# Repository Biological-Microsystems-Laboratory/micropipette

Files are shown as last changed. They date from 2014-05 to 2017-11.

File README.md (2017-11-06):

3D Printable Micropipette
=========================

This printable micropipette actuates a disposable syringe to an adjustable set-point using an assembly of 3D-printable parts and basic hardware.





## Parts

Both the 30-300 uL Pipette and the 100-1000 uL Pipette use the same printed parts: body-clip.stl and plunger.stl. In addition a disposable syringe and some additional hardware is used to assemble the pipette.

**30-300 uL Pipette:**

| Part                                  | Source            | Part Number | Unit Price |
|---------------------------------------|-------------------|-------------|------------|
| Filament                              | Makerbot          | NA          | $1.63      |
| 1 mL Syringe                          | BD Biosciences    | 309628      | $0.15      |
| M3 Bolt, 35 mm                        | McMaster-Carr     | 91287A026   | $0.12      |
| M3 Nut                                | McMaster-Carr     | 90591A121   | $0.01      |
| Music Wire Compression Springs* (2)   | Jones Spring Co   | C10-022-048 | $1.23      |
| Female Luer to 1/8" Hose Barb Adapter | Cole-Parmer       | EW-30800-08 | $0.40      |
| Tygon Tubing, 1/16"ID x 3/16"OD       | Cole-Parmer       | EW-06407-72 | $0.03      |
| 300 uL Tips (10)                      | Fisher Scientific | 02-707-447  | $0.34      |
|                                       | **Total**         |             | **$3.91**  |

**100-1000 uL Pipette:**

| Part                                   | Source            | Part Number | Unit Price |
|----------------------------------------|-------------------|-------------|------------|
| Filament                               | Makerbot          | NA          | $1.63      |
| 3 mL Syringe                           | BD Biosciences    | 309657      | $0.73      |
| M3 Bolt, 35 mm                         | McMaster-Carr     | 91287A026   | $0.12      |
| M3 Nut                                 | McMaster-Carr     | 90591A121   | $0.01      |
| Music Wire Compression Springs* (2)    | Jones Spring Co   | C10-022-048 | $1.23      |
| Female luer to 5/32" Hose Barb Adapter | Cole-Parmer       | EW-45508-06 | $0.66      |
| Tygon Tubing, 1/8"ID x 1/4"OD          | Cole-Parmer       | EW-06407-76 | $0.05      |
| 1000 uL Tips (10)                      | Fisher Scientific | 02-707-400  | $0.41      |
|                                        | **Total**         |             | **$4.84**  |

*Spring Specifications: Overall length 38 mm, OD 7.62 mm, wire diameter 0.56 mm, Max load 0.86 kg, with closed and flat ends. Also avalible from McMaster-Carr P/N: 9657K347.

Kits can also be ordered from: https://www.gogomicro.com

## Assembly and Operation

Assembly: https://www.youtube.com/watch?v=kmtHi_KYfWw

Operation: https://www.youtube.com/watch?v=2W-8hwV7r3c

## Paste on Scale

For ease of use and to achieve the highest accuracy replace the syringe graduations with the adjusted scale. Print out on a transparency sheet and tape on to the syringe aligning the zero point with the plunger position.

## Validation

Data from a commercial pipette and our printed pipette with and without the adjusted print-and-paste scale compared to the ISO standard.

**100-1000 uL pipette:**

|         |                       | Mean    | Systematic Error | \% Sys. err. | Random Error | \% Rand. err. |
|---------|-----------------------|---------|------------------|--------------|--------------|---------------|
| 1000 uL | ISO 8655, 100-1000 uL | 1000    | 8.00             | 0.80         | 3.00         | 0.30          |
|         | Commercial Pipette    | 1002.98 | 2.98             | 0.30         | 1.72         | 0.17          |
|         | Printed Pipette       | 949.29  | -50.71           | -5.07        | 0.60         | 0.06          |
|         | Printed Pipette Scale | 1003.57 | 3.57             | 0.36         | 0.89         | 0.09          |
|         |                       |         |                  |              |              |               |
| 500 uL  | ISO 8655, 100-1000 uL | 500     | 8.00             | 1.60         | 3.00         | 0.60          |
|         | Commercial Pipette    | 503.67  | 3.67             | 0.73         | 0.49         | 0.10          |
|         | Printed Pipette       | 475.99  | -24.01           | -4.80        | 4.75         | 1.00          |
|         | Printed Pipette Scale | 503.62  | 3.62             | 0.72         | 1.64         | 0.33          |
|         |                       |         |                  |              |              |               |
| 200 uL  | ISO 8655, 100-1000 uL | 200     | 8.00             | 4.00         | 3.00         | 1.50          |
|         | Commercial Pipette    | 204.61  | 4.61             | 2.30         | 0.15         | 0.07          |
|         | Printed Pipette       | 186.55  | -13.45           | -6.72        | 1.31         | 0.70          |
|         | Printed Pipette Scale | 201.87  | 1.87             | 0.94         | 1.47         | 0.73          |
|         |                       |         |                  |              |              |               |
| 100 uL  | ISO 8655, 100-1000 uL | 100     | 8.00             | 8.00         | 3.00         | 3.00          |
|         | Commercial Pipette    | 104.29  | 4.29             | 4.29         | 1.65         | 1.58          |
|         | Printed Pipette       | 94.02   | -5.98            | -5.98        | 4.81         | 5.12          |
|         | Printed Pipette Scale | 101.00  | 1.00             | 1.00         | 1.05         | 1.04          |

**30-300 uL pipette:**

|        |                       | Mean   | Systematic Error | \% Sys. err. | Random Error | \% Rand. err. |
|--------|-----------------------|--------|------------------|--------------|--------------|---------------|
| 300 uL | ISO 8655, 30-300 uL   | 300    | 4.00             | 1.33         | 1.50         | 0.50          |
|        | Commercial Pipette    | 301.19 | 1.19             | 0.40         | 0.53         | 0.18          |
|        | Printed Pipette       | 286.91 | -13.09           | -4.36        | 0.42         | 0.15          |
|        | Printed Pipette Scale | 299.11 | -0.89            | -0.30        | 0.48         | 0.16          |
|        |                       |        |                  |              |              |               |
| 200 uL | ISO 8655, 30-300 uL   | 200    | 4                | 2            | 1.5          | 0.75          |
|        | Commercial Pipette    | 200.06 | 0.06             | 0.03         | 0.46         | 0.23          |
|        | Printed Pipette       | 193.40 | -6.60            | -3.30        | 2.86         | 1.48          |
|        | Printed Pipette Scale | 200.57 | 0.57             | 0.28         | 0.86         | 0.43          |
|        |                       |        |                  |              |              |               |
| 50 uL  | ISO 8655, 30-300 uL   | 50     | 4                | 8            | 1.5          | 3             |
|        | Commercial Pipette    | 49.02  | -0.98            | -1.96        | 0.10         | 0.20          |
|        | Printed Pipette       | 49.62  | -0.38            | -0.76        | 1.26         | 2.53          |
|        | Printed Pipette Scale | 48.73  | -1.27            | -2.54        | 1.11         | 2.27          |
|        |                       |        |                  |              |              |               |
| 30 uL  | ISO 8655, 30-300 uL   | 30     | 4                | 13.3         | 1.5          | 5             |
|        | Commercial Pipette    | 29.08  | -0.92            | -3.06        | 0.09         | 0.31          |
|        | Printed Pipette       | 29.22  | -0.78            | -2.59        | 0.31         | 1.07          |
|        | Printed Pipette Scale | 27.78  | -2.22            | -7.41        | 1.37         | 4.93          |
|        |                       |        |                  |              |              |               |
| 20 uL* | ISO 8655, 30-300 uL   | 20     | 4                | 20           | 1.5          | 7.5           |
|        | Commercial Pipette    | NA     | NA               | NA           | NA           | NA            |
|        | Printed Pipette       | 18.70  | -1.30            | -6.48        | 0.38         | 2.01          |
|        | Printed Pipette Scale | 17.94  | -2.06            | -10.29       | 1.87         | 10.42         |
|        |                       |        |                  |              |              |               |
| 10 uL* | ISO 8655, 30-300 uL   | 10     | 4                | 40           | 1.5          | 15            |
|        | Commercial Pipette    | NA     | NA               | NA           | NA           | NA            |
|        | Printed Pipette       | 11.95  | 1.95             | 19.52        | 0.73         | 6.08          |
|        | Printed Pipette Scale | 7.64   | -2.36            | -23.64       | 0.38         | 4.92          |

* *these volumes are outside of 30-300 uL but we wanted to show data in this range achievable by the pipette.*

Check out our write-up in BioRxiv: http://biorxiv.org/content/early/2017/02/20/109231

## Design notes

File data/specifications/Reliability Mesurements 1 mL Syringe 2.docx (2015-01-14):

9/03/2014

Measurements for Test Micropipette compared to 100uL to 1000uL and 10uL to 100uL micropipettes

Trial # | 100uL to 1000uL Micropipette Weight of 200uL of Water dispensed (g) | Test Pipette (1mL Syringe) Weight of 200uL of Water dispensed (g)
1 | 0.2028 | 0.1994
2 | 0.2044 | 0.2001
3 | 0.2014 | 0.1997
4 | 0.2004 | 0.1995
5 | 0.2010 | 0.1962

Trial # | 10uL to 100uL Micropipette Weight of 50uL of Water dispensed (g) | Test Pipette (1mL Syringe) Weight of 50uL of Water dispensed (g)
1 | 0.0496 | 0.0516
2 | 0.0498 | 0.0514
3 | 0.0498 | 0.0517
4 | 0.0500 | 0.0516
5 | 0.0501 | 0.0513

Trial # | 10uL to 100uL Micropipette Weight of 20uL of Water dispensed (g) | Test Pipette (1mL Syringe) Weight of 20uL of Water dispensed (g)
1 | 0.0198 | 0.0195
2 | 0.0196 | 0.0196
3 | 0.0200 | 0.0196
4 | 0.0200 | 0.0195
5 | 0.0199 | 0.0196

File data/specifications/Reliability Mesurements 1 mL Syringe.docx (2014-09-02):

9/02/2014

Measurements for Test Micropipette compared to 100uL to 1000uL and 10uL to 100uL micropipettes

Trial # | 100uL to 1000uL Micropipette Weight of 200uL of Water dispensed (g) | Test Pipette (1mL Syringe) Weight of 200uL of Water dispensed (g)
1 | 0.2052 | 0.1929
2 | 0.2082 | 0.1928
3 | 0.2065 | 0.1922
4 | 0.2075 | 0.2072
5 | 0.2072 | 0.1922
6 | 0.2064 | 0.1924

Trial # | 10uL to 100uL Micropipette Weight of 50uL of Water dispensed (g) | Test Pipette (1mL Syringe) Weight of 50uL of Water dispensed (g)
1 | 0.0500 | 0.0571
2 | 0.0499 | 0.0546
3 | 0.0499 | 0.0535
4 | 0.0499 | 0.0540
5

Trial # | 10uL to 100uL Micropipette Weight of 20uL of Water dispensed (g) | Test Pipette (1mL Syringe) Weight of 20uL of Water dispensed (g)
1 | 0.0198 | 0.0192
2 | 0.0196 | 0.0190
3 | 0.0200 | 0.0184
4 | 0.0200 | 0.0187
5 | 0.0200 | 0.0190

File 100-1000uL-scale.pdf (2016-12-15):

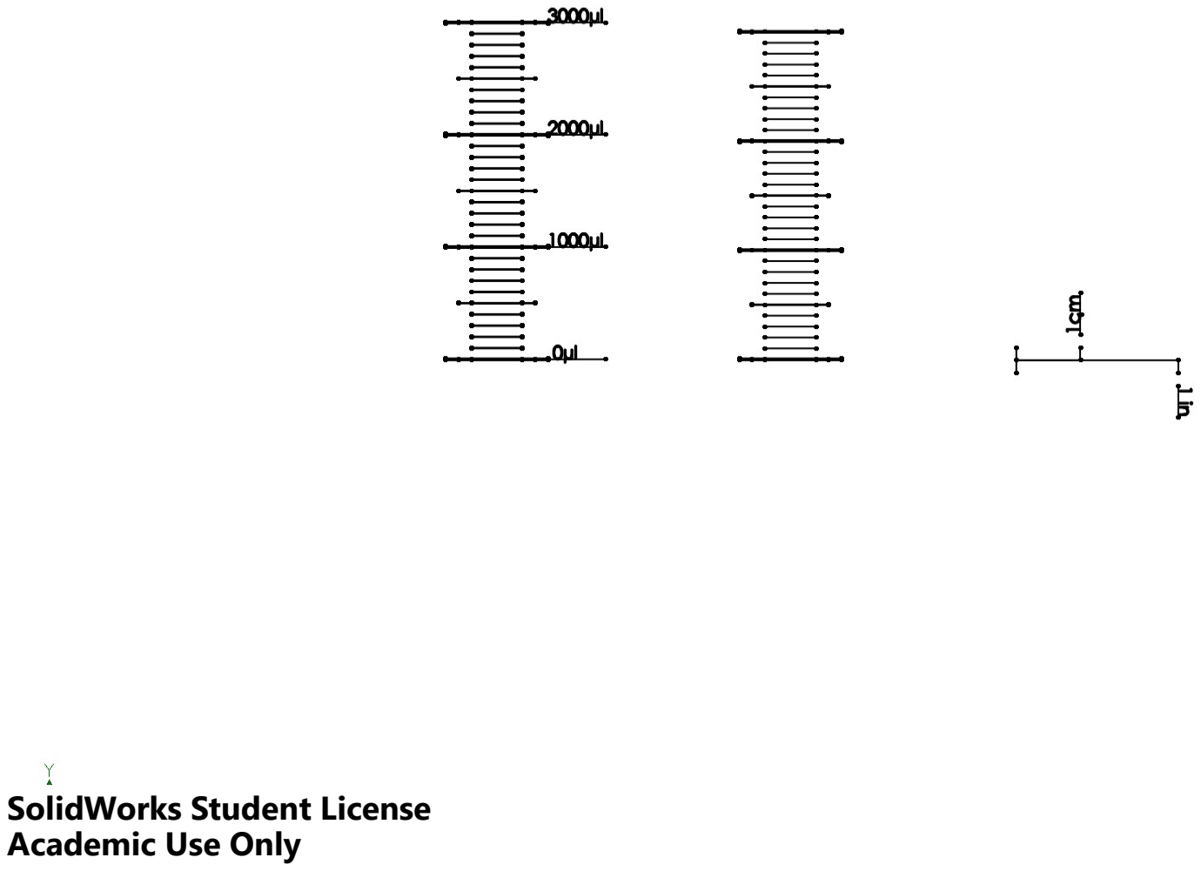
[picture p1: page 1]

SolidWorks Student License Academic Use Only

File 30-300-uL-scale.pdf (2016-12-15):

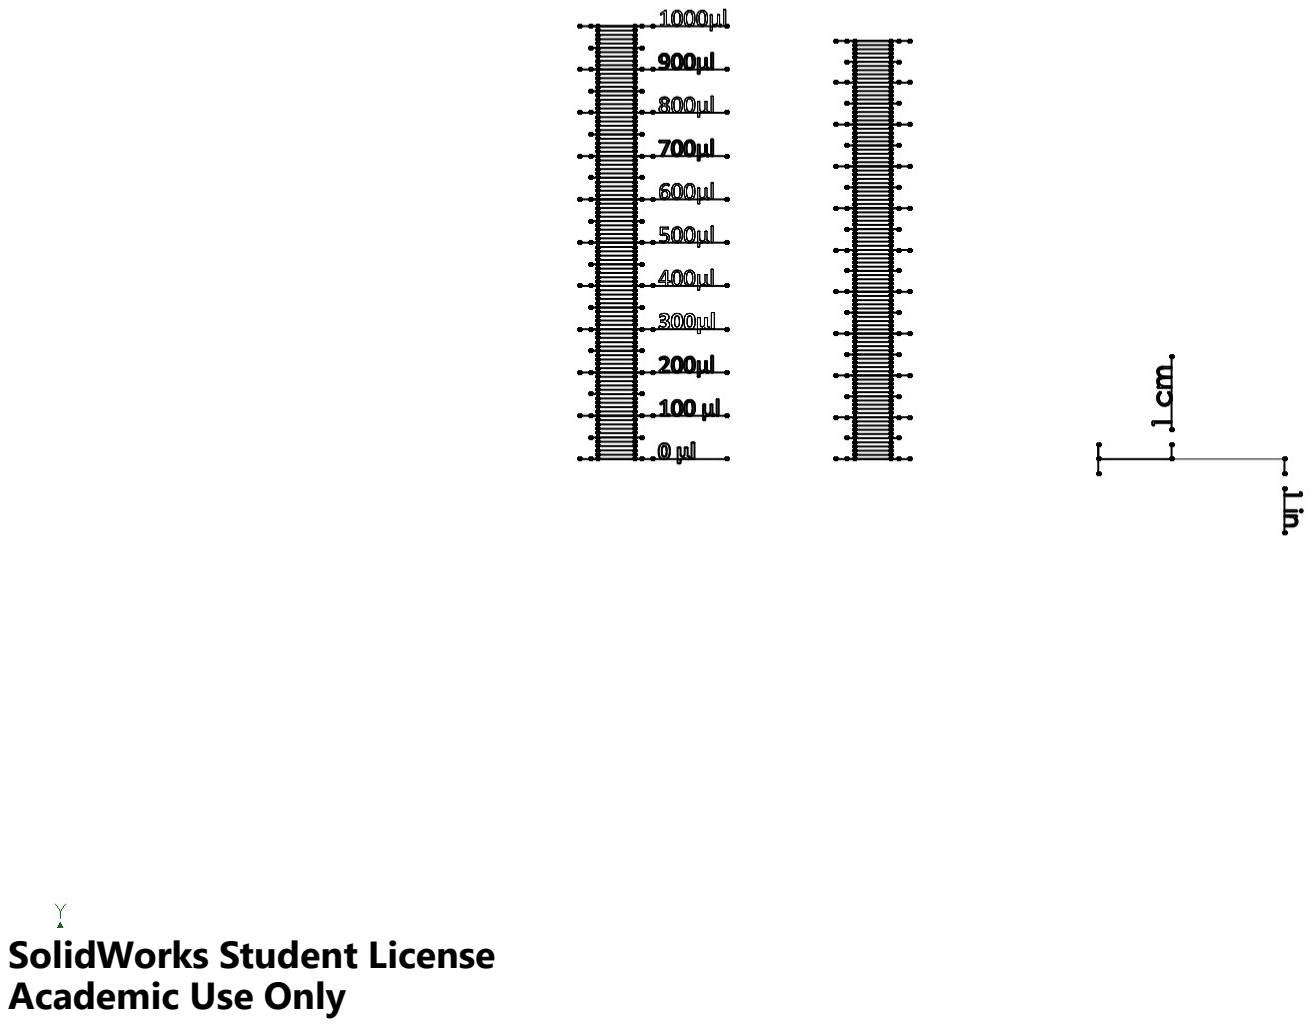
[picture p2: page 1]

SolidWorks Student License Academic Use Only

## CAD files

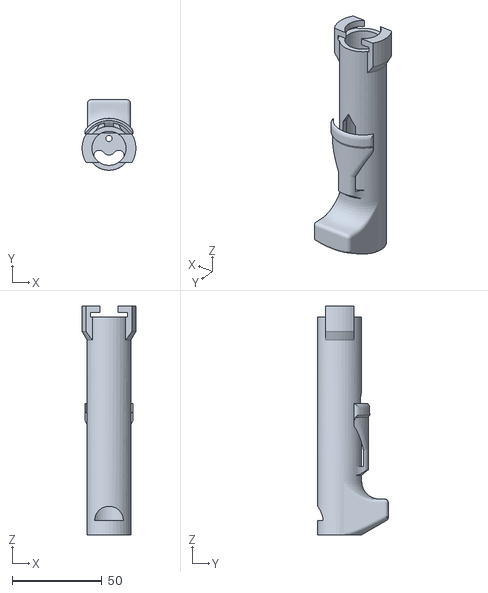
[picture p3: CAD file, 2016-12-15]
body-clip.STL
29.9 x 39.3 x 127.5

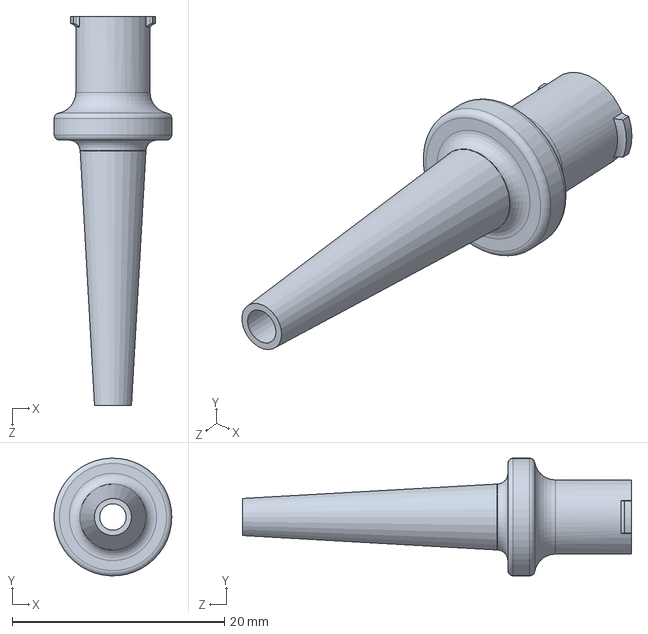
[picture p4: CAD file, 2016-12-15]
CAD-working-files/luer-lock.SLDPRT
11.1 x 11.1 x 36.6 mm

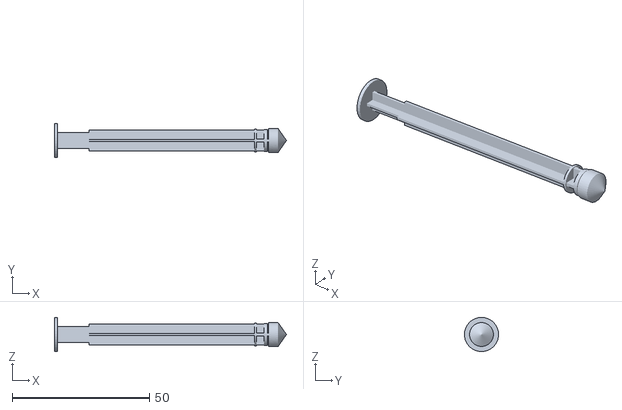
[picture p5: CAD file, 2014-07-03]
CAD-working-files/additional-parts/syringe_plunger.STL
84.6 x 12.5 x 12.5

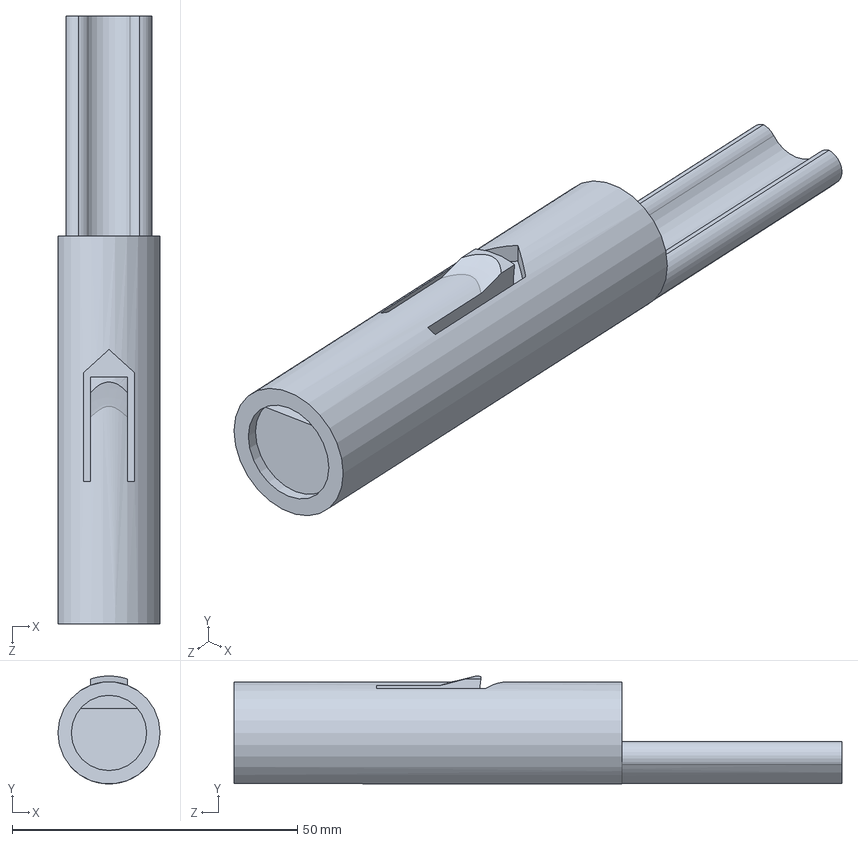
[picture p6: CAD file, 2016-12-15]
CAD-working-files/plunger.SLDPRT
17.9 x 18.9 x 106.5 mm

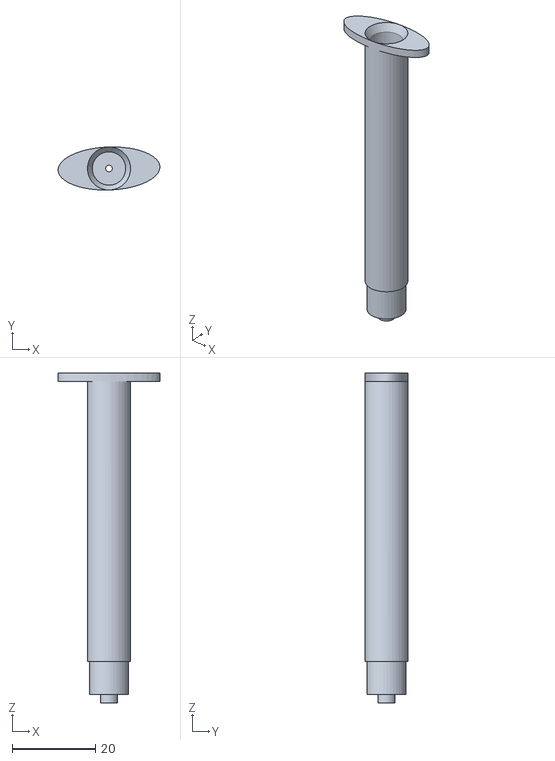
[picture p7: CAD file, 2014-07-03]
CAD-working-files/additional-parts/syringe_barrel.STL
24.4 x 10.4 x 79.2

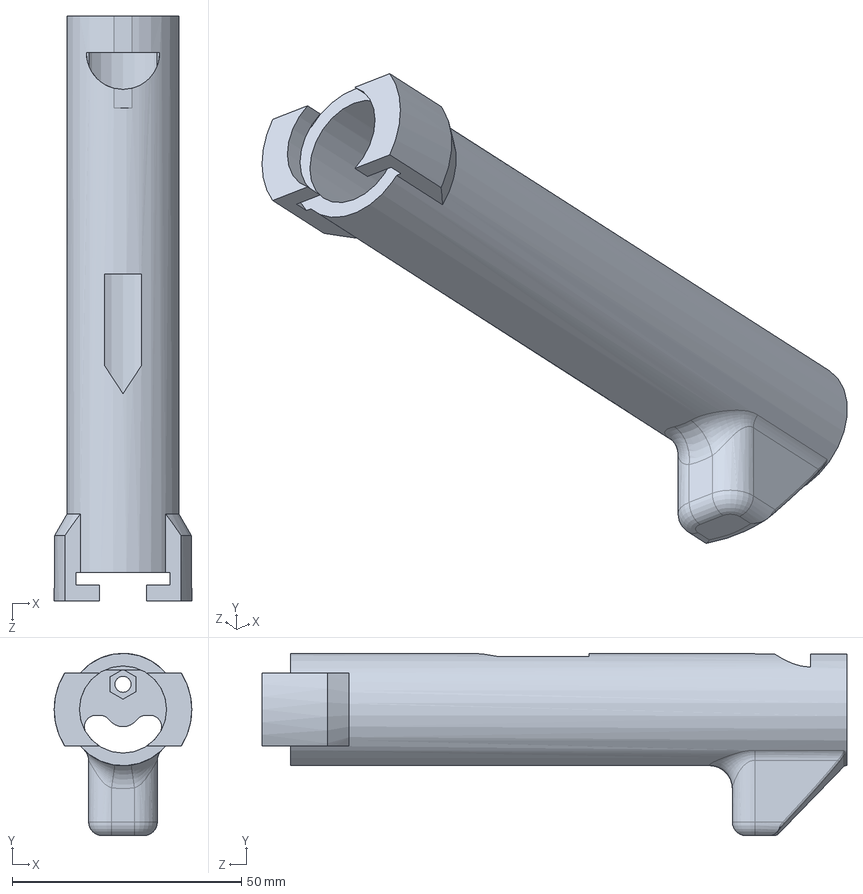
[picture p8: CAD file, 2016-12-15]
CAD-working-files/body-new-lock.SLDPRT
30.0 x 39.8 x 127.5 mm

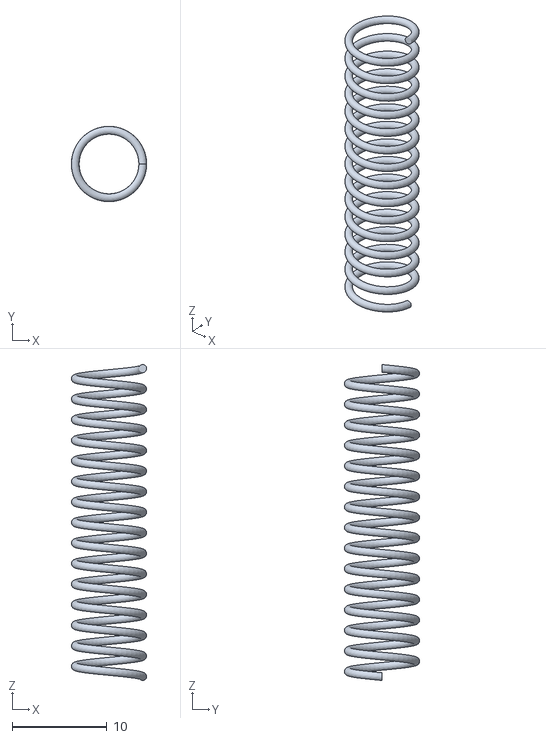
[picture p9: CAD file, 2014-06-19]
CAD-working-files/additional-parts/spring.STL
7.94 x 7.94 x 33.3

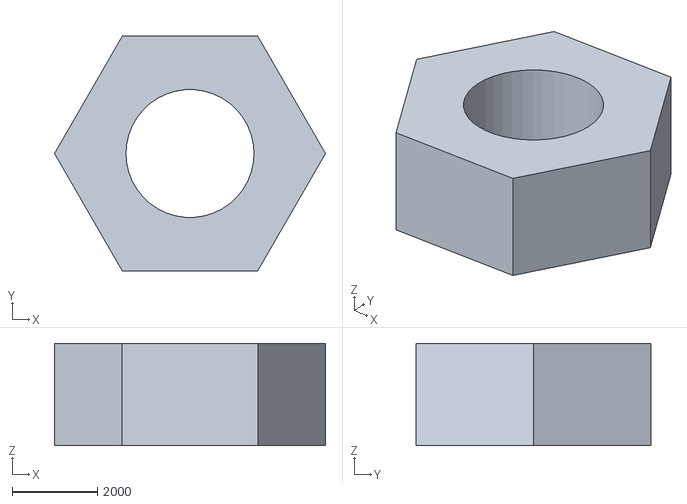
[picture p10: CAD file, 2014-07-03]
CAD-working-files/additional-parts/nut.STL
6350.9 x 5500.0 x 2400.0

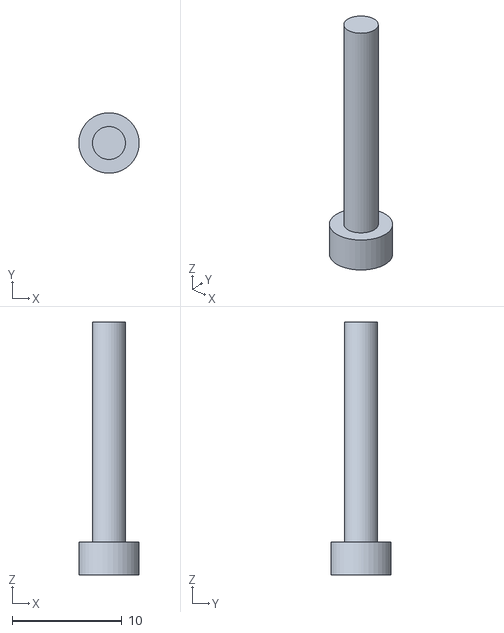
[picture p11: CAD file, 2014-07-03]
CAD-working-files/additional-parts/screw.STL
5.50 x 5.50 x 23.0

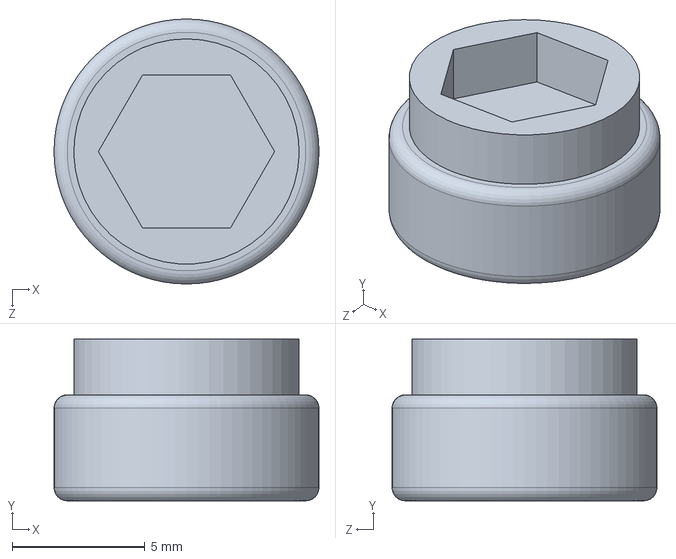
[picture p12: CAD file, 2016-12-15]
CAD-working-files/screw-head.SLDPRT
10.0 x 6.10 x 10.0 mm

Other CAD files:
plunger.STL
CAD-working-files/body-clip.SLDPRT

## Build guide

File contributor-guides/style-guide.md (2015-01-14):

Style Guide
==========

File Nameing Conventions
---------

All file names in lower case with no spaces. Dashes can be used to seperate words. (File extensions may be upper or lower case) 

example:

	wrong: 

	This is a Part.STL

	Right: 

	this-is-a-part.STL

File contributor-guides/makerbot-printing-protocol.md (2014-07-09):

#Printing on the Makerbot
1. export file into .stl format
2. repair file in Meshlab
3. add file(s) into Makerbot Desktop Software
4. export to a .makerbot file on to a USB drive
5. plug the USB drive into the Makerbot and follow the onscreen instructions.
6. After printing has started moniter the printer (about 15-20min) to assure the part is printing properly.

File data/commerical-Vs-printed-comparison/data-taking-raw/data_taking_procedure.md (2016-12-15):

#Data taking procedure:

##Day before

Set up the scale on a vibration isolated table (optics air-table).

Place a 50 mL cup of deionized water and a thermometer near the scale the day before to equilibrate to room temperature.

##Day of data recording:

*note: All pipetting/dispensing should be done with the pipette completely vertical.*

**Preform evaporation loss procedure for 10 and 20 uL:** To determine mass loss, dispense water into the weighing vessel, note the reading and begin timing with a stop watch. Check how much the reading decreases during 30 seconds. Compare this to the pipetting. Typically, the pipetting time might be 10 seconds and the mass loss is
2 mg.

Record the water and room temperature as well as the relative humidity.

##Commercial Pipette

**With Eppendorf 200 uL pipette:**

1. Set to 200
2. pre-wet tip
3. pipette and record 5 times
4. set to 50 
5. repeat 2-3
6. set to 20
7. repeat 2-3
8. get a new tip, repeat 1-7
9. get a new tip, repeat 1-7

**With an Fisherbrand 10-100 uL pipette:**

1. Set to 10
2. pre-wet tip
3. pipette and record 5 times
4. get a new tip, repeat 1-3
5. get a new tip, repeat 1-3

Data will be 3 trials (N=3) at each volume with 5 measurements.

##Printed Pipette

**Person pipetting shall not see the scale read-out.**

1. set to 200
2. pre-wet
3. pipette and record 5 times
4. set to 50
5. repeat 2-3
6. set to 20
7. repeat 2-3
8. put on 20 uL pipette
9. set to 10 uL
10. repeat 2-3
11. put on a new 200 uL tip and repeat 1-10
12. put on a new 200 uL tip and repeat 1-10 (Maybe switch to another user)

Each user will complete steps 1-12, giving an n=3 for each user.

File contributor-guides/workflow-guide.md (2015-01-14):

master branch
-------------
This is the default branch.
This is the first branch that everyone sees when they visit the project repository.
This will contain the most recently released version of the working tested parts along with relevant documentation for this specific version. 

develop branch
--------------
This is a staging branch for the master branch.
Assume that the develop branch may be merged into the master branch at anytime.
Do all actual work in a new branch from the develop branch and then clean it up before merging it back into the develop branch.

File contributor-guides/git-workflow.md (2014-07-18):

Working with git protocol:
==========================

1. get to the working directory and pull down changes from the origin repository when starting work

		$ git pull

If you lost the directory from last time or are getting merge errors start a fresh directory by cloning to make a new directory. You can then add any new files that you were working on. 

		$ git clone https://github.com/mbrenn3/Volvox-C-section.git

2. Start working. Save and  commit changes often.

		$ git commit -am "concise commit comment"

3. To add new files that you want to track.

		$ git add newfile.txt

4. push changes to the server periodically, at least at the end of the day. 

		$ git push origin branch-name

If your push was rejected someone else has already pushed changes pull down to merge your work, and push again

		$ git pull
		$ git push origin branch-name

The following is a more detailed reference for using git and git hub: 

Git and Github
===

[This](http://git-scm.com/book/en/Getting-Started) book is the best. 

Install git: [http://git-scm.com/downloads](http://git-scm.com/downloads)

Initial set-up
-------
###First set up your identity

Start a new folder and cd to it, then check settings:

To set up identity: 
	
	$ git config --global user.name "John Doe"
	$ git config --global user.email johndoe@example.com
	
To list identity and settings
	
	$ git config --list
	
###Initialize a repository, add a readme, a remote, and push to github

make a new directory and enter it, and make a file 

    $ mkdir test
    $ cd test
    $ touch readme.txt

initialize git

    $ git init
    
check the status of your git repository

    $ git status
    
You should see your readme.txt as an untracked file. Add files that you want to track with

    $ git add <filename.file>

Check status again. Now you should see your file as tracked.

Now we will commit, this will take the first snapshot of all tracked files.

    $ git commit -am "initial commit"
    
(The -a flag skips the staging step which is not important right now and the -m flag allows you to add your commit comment inline with the command rather than opening an editor.)

Now open the text file that you are tracking and enter some info and save it. Now run git status. You should see the file as modified. Now commit again, and check the status again.

    $ git commit -am "second commit"
    
You should see

> On branch master

> nothing to commit (working directory clean)

Now to look back and see what you did, run 

    $ git log
    
You should see two entries listing the commit hash, which will be how you refer to the commit internally, as well as yourself as the author, the date and you commit comment. 

Now lets make a mirror of this repo on github. Login to git hub in your browser and make a new repository. Name it the same as the directory your working in as your computer, test. Don't initialize with a readme. Now go back to the terminal and add a remote

    $ git remote add origin https://github.com/<username>/<directory>.git
    
Now we are going to push our repository onto the cloud (Github).

    $ git push -u origin master
    
This is telling git to copy changes to origin (the Github repository) from master (the local repository your working with). The -u flag just tells git to remember parameters so next time you can just run git push. 

Now so you can see that everything is working go to the repository in Github. You should see your readme.txt in your test repository. Now edit it and commit changes in Github and go back to the terminal.

    $ git pull
    
You should see git download the changes you made and now when you look at the file on your computer it will include the edits you made through Github. Yay! also when you run git log you will see your edit and commit that you made.

Using the Develop Branch

1. when working on a file, pull from the Branch Develop. This will sychronize your local files with the latest files on GitHub.

2. Start working on the files in your local folder. As you are working commit the changes on the Git Hub windows with short comments. 

3.When you finish a product/item then go to branch master by
git checkout branch master
then merge the develp branch into master.

4. You can also add branches and form new branches after pulling from Develop. Then you must merge that branch in to develop and and then into master. This keeps the master branch clean.

Remotes
---

###Clone an Existing Repository: 

	$ git clone https://github.com/mbrenn3/3D-printed-oxygen-devices.git

This will make a directory named 3D-printed-oxygen-devices with the project file inside it.

###When you are done working push back to the origin (Github)

	$ git push -u origin master

###Before you start working later pull changes to the local repo

	$ git pull origin
	
Branching
---------
Until now  all work has been done in the Master branch. Lets try to keep the master branch as a latest working/final version, and do all work in branches. When your work in a branch is ready to present we can merge it to the master, don't worry it's very easy. [This](http://git-scm.com/book/en/Git-Branching-What-a-Branch-Is) page is really helpful

To create a branch

    $ git branch new

Now you have created a branch named "new" that is an exact copy of the branch you are in now. You can move to and start working in that branch by moving the 'HEAD'.

to move the HEAD to branch

    $ git checkout new

You can now work here and make commits in this branch without affecting the master branch (also to clarify, master is just the default name git gives the initial branch of a project). Before you go back and checkout another branch you should always commit your changes and leave with a clean working directory. 
    
To move the HEAD back to master

    $ git checkout master

Now you can merge the branch that you are working on 'new' into master with

    $ git merge new

Now the master branch will have all the changes and updates that you worked on in the new branch. If you are done working on that topic you can delete the branch with

    $ git branch -d new

You can also quickly make a new branch and switch the HEAD to it to start working
    
    $ git checkout -b newer

Basic Commands:
You can check your working dirctory by typing " pwd " in to you Git Bash window.

pwd 

To change the directory on your computer type" cd "

cd 

then list the path to the folder

ex : 
cd Documents/ ...

You can list the directory contents by typing 
 
ls

Access older versions of repositories "Pulled from GitHub"
Go to     
http://githowto.com/getting_old_versions    
for more info

First run this command in Git to set up alias 

	git config --global alias.hist 'log --pretty=format:"%h %ad | %s%d [%an]" --graph --date=short'

then run

git hist
Note: Do not forget to define hist in your .gitconfig file? If you do not remember how, review the lesson on aliases.

Check the log data and find the hash for the first commit. You will find it in the last line of the git hist data. Use the code (its first 7 chars are enough) in the command below. 

RUN:
git checkout <hash>

Note: Many commands depend on the hash values in the repository. Since my hash values will be different from yours, substitute in the appropriate hash value for your repository everytime you see <hash> or <treehash> in the command.

You are in 'detached HEAD' state. You can look around, make experimental
changes and commit them, and you can discard any commits you make in this
state without impacting any branches by performing another checkout.

If you want to create a new branch to retain commits you create, you may
do so (now or later) by using -b with the checkout command again. Example:

  git checkout -b new_branch_name

02 Returning to the latest version in the master branch

RUN:
git checkout master

‘master’ is the name of the default branch. By checking out a branch by name, you go to its lastest version.

Tagging Git
go to
 http://git-scm.com/book/en/Git-Basics-Tagging
for more help

Tagging

Annotated Tags
Creating an annotated tag in Git is simple. The easiest way is to specify -a when you run the tag command:

$ git tag -a v1.4 -m 'my version 1.4'

$ git tag

The -m specifies a tagging message, which is stored with the tag. If you don’t specify a message for an annotated tag, Git launches your editor so you can type it in.

You can see the tag data along with the commit that was tagged by using the git show command:

$ git show v1.4

Sharing Tags

$ git push origin v1.5

If you have a lot of tags that you want to push up at once, you can also use the --tags option to the git push command. This will transfer all of your tags to the remote server that are not already there.

$ git push origin --tags

Now, when someone else clones or pulls from your repository, they will get all your tags as well.

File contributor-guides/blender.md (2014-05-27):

Blender Tutorial
=====

First commands
------

* Click a hold the middle scroll wheel to change view.

* right click to select objects

toggle manipulator (arrows)

	control + space

ortho/perspective view hit space and type "ortho"

TAB to toggle edit mode / object mode

turn measure tool on go to *file > user preferences > addons* check: **3d View: Measure Panel**
	
toggle number display with "N" and click activate, then update measurement when you have two vertices selected.
	
toggle wireframe mode with "Z"

to place the cursor: left click, reset cursor with

	Shift + C 
	
More cursor options with 

	Shift + S	

Undo
	
	CTRL + Z	
	
Manipulating Objects
------

objects can be created with the add menu or 
	
	SHIFT + A
	
Select multipule vertices with "C" then left click, right click to exit. Scroll after hitting "C" to change the size of the selection area. (Maybe handier in wireframe mode "Z")

Draw a box around vertices to select with "B"

Hide selected elements with "H" un-hide with "ALT + H"

Grab to move an object with "G". Lock movement to axis by hitting "X", "Y" or "Z". Lock to two axes at a time, for example X and Y hit ALT + Z, or the remaining axis. 

* to duplicate and object SHIFT + D. The object is now locked in grab. 

* Scale an object with "S". Scaling can be locked to axes as above. 

* Extrude with "E"
	
joining objects

Modifying Surfaces
----

In edit mode you can select and manipulate individual vertices, edges, and faces. 

to delete an object or element "X" or "Delete" will bring up a menu to delete. 
	
Make a face between selected vertices with "F". Create faces alternative faces with "Alt + F" 

The wire loop tool draws a loop of vertices around an object.
	
	CTRL + R 

boolean difference 
------
You create voids in objects with other objects.
Select object in object mode. Click wrench for modifier. With "Add modifier" select Boolean. For "operation" select "difference". Then select the second object under "object". Hit Apply. When you in wireframe edit mode you should new vertices created around the object. 

Conventions
----

units keep 1mm = blender unit 

Saved versions can be enumerated with the "+" sign  at the right of the file name. 

Extra
---

in edit mode "W" brings up a menu to remove doubles

[Good tutorial video](http://www.youtube.com/watch?v=dIAO1zS6oGY) for 3D printing parts. His second video is greate too.

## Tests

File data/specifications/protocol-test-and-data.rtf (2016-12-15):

protocol for data and tests:

The pipettes accuracy was tested by obtaining 15 measurements at 4 different settings: 10ul, 20uL, 50uL, and 200uL. After each trial the screw was reset and readjusted to the same measurement. The experimenter solely used his eyes to adjust the pipette. The values form each trial were compared to the values of a commercial pipette. The percent error from the theoretical values and standard deviation were used to determine the accuracy and precision of both pipettes.

Steps Test Pipette Accuracy
1. Place a weight boat onto the scale and zero the scale
2. Set the micropipette to 200uL
a. This is done by noting the initial position of the syringe in the lock position then adding 200uL or 0.2 mL to that initial position.
3. Place the tip in distilled water and pipette the water about 3 times to prewet the tip.
4. Then pipette 200uL onto the weight boat.
5 .Record the value.
6. Adjust the Screw if necessary.
7. Set it back to 200uL like described in step 2.
8. Perform steps 3-5 until we have 15 measurements.
(The same steps were used to obtain data for the 10uL, 20uL, and 50uL measurements.)
Steps Commercial Pipette Accuracy
1. Place a weight boat onto the scale and zero the scale
2. Set the 100-1000uL micropipette to 200uL.
3. Place the tip in distilled water and pipette the water about 3 times to prewet the tip.
4. Then pipette 200uL onto the weight boat.
5. Record the value.
6. Repeat Steps 3-5unitil we have 15 measurements
(The same steps were used to obtain data for the 10uL, 20uL, and 50uL measurements but instead the 10-100uL micropipette was used)
Steps Test Precision
Test Pipette
1. Set the micropipette to 200uL
a. This is done noting the initial position of the syringe in the lock position then adding 200uL to that initial position.
2. Place the tip in distilled water and pipette the water about 3 times to prewet the tip.
3. Then pipette 200uL onto the weight boat.
4 .Record the value.
5. Repeat this step until we have 50 measurements
Commercial Pipette
1. Set the micropipette to 200uL
2. Place the tip in distilled water and pipette the water about 3 times to prewet the tip.
3. Then pipette 200uL onto the weight boat.
4 .Record the value.
5. Repeat this step until we have 50 measurements

Calculations
Accuracy Systematic Error:
To calculate the systematic error, the mean from the novice user’s trial was subtracted from the accepted value, then divided by the accepted value.

Precision Random Error:
To test precision, the mean was subtracted from the largest deviation from the mean.

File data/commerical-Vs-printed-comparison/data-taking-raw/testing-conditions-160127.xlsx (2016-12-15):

Time | Mass (mg) 10uL | Mass 20uL | Room Temp | AP | Humidity | Converstion ul/mg
0 | 9.5 |  | 23.9c | 102 kpa | low | 1.0038
30 | 9.4
60 | 9.3
90 | 9
120 | 8.9
150
180
210
240
270
300
Time | Mass (mg) 10uL | Mass 20uL
0 | 9.8
30 | 9.3
60 | 9.1
90 | 8.8
120 | 8.5
150
180
210
240
270
300

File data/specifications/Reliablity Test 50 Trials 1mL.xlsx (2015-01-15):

Trial | Amount Dispensed 100-1000uL Pipette (g) | Amount Dispensed Experimental (1mL)Pipette (g) | Normal Distribution
1 | 0.2026 | 0.195 | 0.1913499262
2 |  | 0.1955 | 0.4638516103
3 |  | 0.196 | 0.7553625895
4 |  | 0.1964 | 0.9061176841
5 |  | 0.1953 | 0.3432483067
6 |  | 0.196 | 0.7553625895
7 |  | 0.1954 | 0.4023866109
8 |  | 0.1953 | 0.3432483067
9 |  | 0.195 | 0.1913499262
10 |  | 0.1958 | 0.6475014649
11 |  | 0.1955 | 0.4638516103
12 |  | 0.196 | 0.7553625895
13 |  | 0.1952 | 0.2877214769
14 |  | 0.1959 | 0.7036830807
15 |  | 0.1944 | 0.03502635777
16 |  | 0.1942 | 0.01681632028
17 |  | 0.1959 | 0.7036830807
18 |  | 0.1942 | 0.01681632028
19 |  | 0.1956 | 0.5261934947
20 |  | 0.1958 | 0.6475014649
21 |  | 0.1958 | 0.6475014649
22 |  | 0.195 | 0.1913499262
23 |  | 0.1962 | 0.8423930374
24 |  | 0.1959 | 0.7036830807
25 |  | 0.1958 | 0.6475014649
26 |  | 0.196 | 0.7553625895
27 |  | 0.1953 | 0.3432483067
28 |  | 0.1953 | 0.3432483067
29 |  | 0.1955 | 0.4638516103
30 |  | 0.195 | 0.1913499262
31 |  | 0.1963 | 0.8771345659
32 |  | 0.1964 | 0.9061176841
33 |  | 0.1958 | 0.6475014649
34 |  | 0.1953 | 0.3432483067
35 |  | 0.1952 | 0.2877214769
36 |  | 0.1959 | 0.7036830807
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

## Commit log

2014-05-27 added git workflow, blender tutorial, and initial designs in stl format
    [case.stl, luer-lock.stl, plunger.stl]
2014-05-30 added syringe lock
    [syringe-lock.stl]
2014-05-30 Changed orientation of .stl files for print
    [case.stl, syringe-lock.stl]
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2014-06-06 added new bolts and nuts files
    [Metric Zinc-Plated Steel Hex Nut.SLDPRT, Metric Zinc-Plated Steel Hex Nut.STL, Type 18-8 Stainless Steel Socket Head Cap Screw.SLDPRT, Type 18-8 Stainless Stee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]
2014-06-16 Syringe Plunger
    [Plunger.SLDPRT]
2014-06-16 Syringe Barrel Added
    [Syringe Part Barrel.SLDPRT]
2014-06-16 Added STL files
    [Syringe Part Barrel.SLDPRT]
2014-06-16 Added .STL file for Syringe Barrel
    [Syringe Part Barrel STL.STL, Syringe Part Plunger.STL]
2014-06-16 Syringe Plunger added as an SolidWorks File
    [Syringe Part Plunger.SLDPRT]
2014-06-17 Added syringe dimension without pictures
    [Syringe Measurements.xlsx]
2014-06-17 Added pictures to the syringe reference meas.
    [Syringe Measurements with Pictures.xlsx]
2014-06-17 updated To-Do List
    [Syringe Rendering Assembly.SLDASM]
2014-06-17 Changed Texture
    [Syringe Part Barrel.SLDPRT]
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2014-06-18 Plunger Extended Push Botton
    [Plunger with extended push button stl.STL, Plunger with extended push button.SLDPRT]
2014-06-18 Updated To Do List
    [plunger.stl]
2014-06-18 Renamed and Extented Push button
    [plunger-shaft.stl]
2014-06-18 Renamed to body.stl
    [case.stl]
2014-06-18 Renamed case.stl to body.stl
    [body.stl]
2014-06-19 Made spring for rendering
    [Part Spring.SLDPRT]
2014-06-19 Added STL of Spring
    [Part Spring.STL]
2014-06-19 converted body to sldprt for lock
    [body with integrated lock.SLDPRT]
2014-06-20 started deleting lock hooks
    [body with integrated lock.SLDPRT]
2014-06-23 removed snap-on hooks from body
    [body with integrated lock.SLDPRT]
2014-06-23 converted stl to solidworks for edit
    [syringe-lock solidworks file.SLDPRT]
2014-06-23 Started assembling parts
    [body with integrated lock.SLDPRT]
2014-06-23 Updated cross sections
    [body with integrated lock.SLDPRT]
2014-06-23 updated cross sections for mate
    [syringe-lock solidworks file.SLDPRT]
2014-06-23 finished corss section for mating
    [body with integrated lock.SLDPRT]
2014-06-23 body with integrated syringe lock v1
    [body with integrated lock final 1.SLDASM]
2014-06-23 finished cross sections for mating
    [syringe-lock solidworks file 2.SLDPRT]
2014-06-23 completed cross sections for mating
    [body with integrated lock 2.SLDPRT]
2014-06-24 Started creating integrated syringe lock
    [body with integrated lock.SLDPRT]
2014-06-24 added lock to body "needs round extrude cut"
    [body with integrated lock.SLDPRT]
2014-06-24 scaled body to mm from Meters
    [body with integrated lock scaled.SLDPRT]
2014-06-24 converted scaled body to STL
    [body with integrated lock scaled stl.STL]
2014-06-25 started adding round groove in lock
    [body with integrated lock scaled.SLDPRT]
2014-06-25 Final Finished adding lock to body with scalling
    [body with integrated lock scaled.SLDPRT]
2014-06-25 Final Solid Work part body with lock
    [Final body with integrated lock scaled.SLDPRT]
2014-06-25 Converted final body to stl for rendering
    [Final body with integrated lock scaled STL.STL]
2014-06-25 extended plunger and scaled part
    [Plunger with extended push button.SLDPRT]
2014-06-25 Final plunger with extended button scaled
    [Scaled Plunger with extended push button.SLDPRT]
2014-06-26 scaled plunger with extended push button
    [Scaled Plunger with extended push button.SLDPRT]
2014-06-26 Assembly for Plunger and Body for Rendering
    [Assembly of Body with Plunger Final Rendering.SLDASM]
2014-06-26 Mated Plunger with Body for Rendering
    [Assembly of Body with Plunger Final Rendering.SLDASM]
2014-06-26 Added flat bottom
    [Scaled Plunger with extended push button.SLDPRT]
2014-06-26 Added flat bottom and Limited Button Movement
    [Scaled Plunger with extended push button STL 2.STL]
2014-06-26 Plunger Solidworks file with flat bottom
    [Scaled Plunger with extended push button 3.SLDPRT]
2014-06-26 STL for plunger with flat bottom and limited button
    [Scaled Plunger with extended push button 3 stl.STL]
2014-06-26 Modified Body with locking mechanism
    [Final body with lock.SLDPRT, body.SLDPRT]
2014-06-26 integrated locking mechanism to body
    [body.SLDPRT]
2014-06-26 integraded locking mechanism
    [body.stl]
2014-06-26 body with lock
    [body.SLDPRT]
2014-06-26 Intergrated lock to body
    [body.SLDPRT]
2014-06-30 Clean up branch
    [Assembly of Body with Plunger Final Rendering.SLDASM, Final body with integrated lock scaled STL.STL, Final body with integrated lock scaled.SLDPRT, Final body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]
2014-07-01 Other files for editing parts in solidworks
    [Assembly of Body with Plunger Final Rendering.SLDASM, Final body with integrated lock scaled STL.STL, Final body with integrated lock scaled.SLDPRT, Final body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]
2014-07-03 converted files to non-binary
    [Metric Zinc-Plated Steel Hex Nut.STL, Syringe Part Barrel STL.STL, Syringe Part Plunger.STL, Type 18-8 Stainless Steel Socket Head Cap Screw.STL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]
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2014-07-16 extended 4 longer body, hollow tube, button limit
    [plunger-shaft.stl]
2014-07-16 Solidworks file with updated plunger
    [Scaled Plunger with extended push button 3.SLDPRT]
2014-07-16 Plunger files for edditing in solidworks
    [Scaled Plunger with extended push button 4.SLDPRT, plunger-shaft.SLDPRT]
2014-07-16 Made the lock in body stonger, added SLDPRT files for edit
    [body 111.SLDPRT, body with stonger lock.SLDPRT, body.SLDPRT, body.stl]
2014-07-17 body with a stonger syringe lock
    [body.SLDPRT]
2014-07-18 SLDPRT for future editing
    [body.SLDPRT, plunger-shaft.SLDPRT]
2014-07-21 Solidworks edit file
    [body.SLDPRT]
2014-07-21 sld part for edit
    [plunger-shaft.SLDPRT]
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2014-07-24 incomplete 1mL body
    [body 1mL.SLDPRT]
2014-07-24 Added 1mL Syringe Plunger
    [plunger-shaft 1mL.SLDPRT]
2014-07-28 Added Charts and Graphs
    [1mL Micropipette Displacement vs Dispensed amount.xlsx, 3mL Micropipette Displacement vs Dispensed amount.xlsx]
2014-07-28 added adjustable regions
    [3mL Micropipette Displacement vs Dispensed amount.xlsx]
2014-07-28 updated mesurements
    [3mL Micropipette Displacement vs Dispensed amount.xlsx]
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2014-07-30 Started editing body for 1mL pipette with more cap?
    [body 1mL.SLDPRT]
2014-07-30 started extending body
    [body 1mL.SLDPRT]
2014-07-31 Scaled luer-lock and saved a nonbinary
    [luer-lock.SLDPRT, luer-lock.stl]
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2014-08-04 Added mesurements and accuracy
    [1 mL Pipette Mesurements.xlsx]
2014-08-06 Fixed locking turn, extended for dispensing
    [body.SLDPRT]
2014-08-07 extended plunger-shaft
    [plunger-shaft.SLDPRT]
2014-08-08 updated parts for extra dispensing
    [body.stl, plunger-shaft.stl]
2014-08-11 verified size
    [luer-lock.SLDPRT]
2014-08-11 added hook to body
    [body.SLDPRT, body.stl]
2014-08-11 fillet top edges
    [body.stl]
2014-09-02 Added reliablility mesuremetnts #1
    [Reliability Mesurements 1 mL Syringe Excel.xlsx, body-with-hook.SLDPRT]
2014-09-03 added new set of trials
    [Reliability Mesurements 1 mL Syringe Excel 1-2.xlsx, Reliability Mesurements 1 mL Syringe Excel.xlsx]
2014-09-03 added 3rd trial
    [Reliability Mesurements 1 mL Syringe Excel 1-2.xlsx]
2014-09-10 added trials to test drift
    [Reliablity Test 50 Trials 1mL.xlsx]
2014-09-16 added charts
    [Reliability Mesurements 1 mL Syringe Excel 1-2.xlsx, Reliablity Test 50 Trials 1mL.xlsx]
2014-09-16 added presenetation
    [Micropipette Presentation.xlsx, Reliablity Test 50 Trials 1mL.xlsx]
2014-09-16 added precision and acuracy values
    [Micropipette Presentation.xlsx]
2014-09-16 presentation and charts
    [Micropipette Presentation.xlsx, Reliability Mesurements 1 mL Syringe Excel 1-2.xlsx]
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2014-10-09 started user-data analysis, started luerlock fix
    [Micropipette Presentation.xlsx, luer-lock.SLDPRT, user-data-analysis-graphs.xlsx]
2014-10-14 fixed luer-lock and nonbinary
    [luer-lock.SLDPRT, luer-lock.STL]
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2014-11-04 fixed luer-lock, added angle correspondence
    [Turns vs Dispensed.xlsx, luer-lock.SLDPRT, luer-lock.STL]
2014-11-04 fixed luer-lock
    [luer-lock.SLDPRT, luer-lock.STL]
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2015-01-14 added luer-lock fix
    [Turns vs Dispensed.xlsx, luer-lock-new.SLDPRT, luer-lock-new.STL]
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2015-06-03 replaced stl files
    [body.STL, plunger.STL]
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2015-06-05 fixed top of plunger
    [body-new-lock.SLDPRT, body.STL, plunger.SLDPRT, plunger.STL]
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2015-06-09 fixed body and flipped plunger
    [body-new-lock.SLDPRT, body.STL, plunger.STL]
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2015-08-26 fixed syringe lock, luer lock, and plunger
    [body-new-lock.SLDPRT, body.STL, luer-lock.SLDPRT, luer-lock.STL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]
2015-08-26 fixed .stl for print
    [luer-lock.SLDPRT, luer-lock.STL, plunger.STL]
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2015-09-08 fixed files
    [body-new-lock.SLDPRT, body.STL, luer-lock.SLDPRT, plunger.SLDPRT]
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
